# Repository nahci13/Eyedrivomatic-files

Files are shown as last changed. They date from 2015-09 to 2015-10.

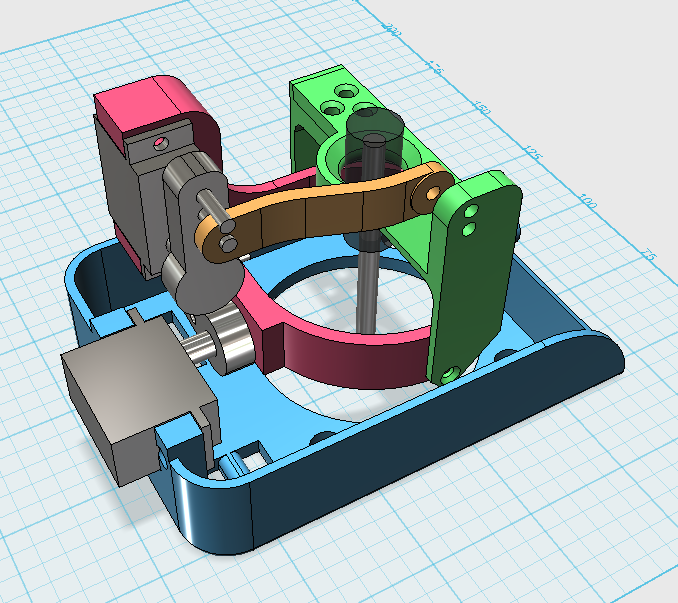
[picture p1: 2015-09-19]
Eyedrivomatic Photos/mk5 electronic hand design.png

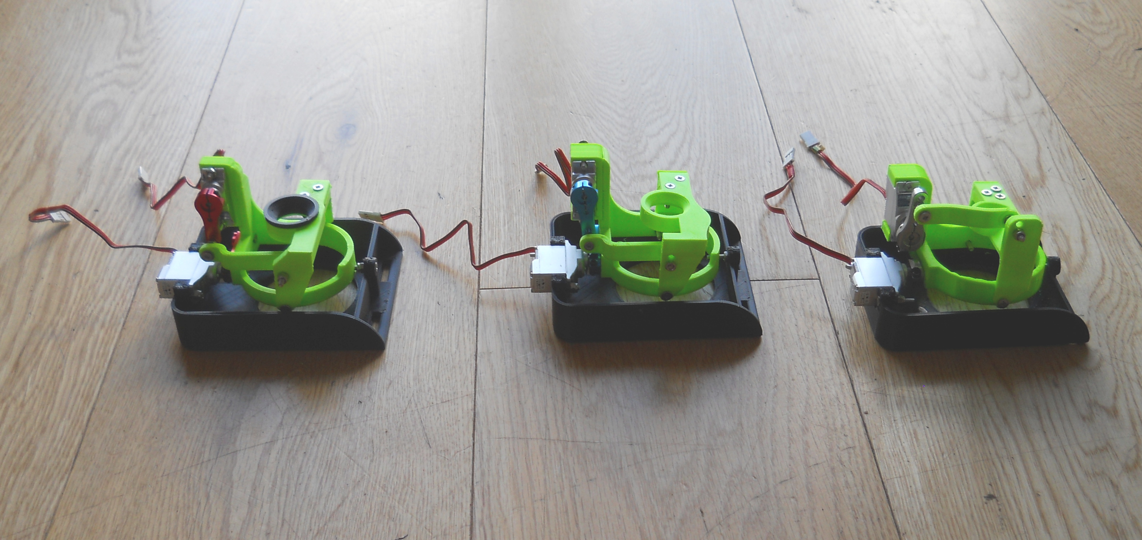
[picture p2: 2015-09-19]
Eyedrivomatic Photos/electronic hand sub prototypes.JPG

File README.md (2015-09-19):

# Eyedrivomatic-Pure
All the files needed to build an Eyedrivomatic system 

Eyedrivomatic is a low cost system to enable quadraplegics to drive an electric wheelchair using only their eyes. In this repository are all the files needed to build an eyedrivomatic system yourself. An eyedrivomatic system is made up of two parts; a 'brain box', and an 'electronic hand'. The electronic hand physicaly pushes the wheelchair's joystick, and the brain box controls it. Software on the users computer, controlled by eyegaze equipment, sends commands to the brain box. 

All the software for the eyedrivomatic project is free software: you can redistribute it and/or modify it under the terms of the GNU General Public License version 3.For more info see http://www.gnu.org/licenses/

all the hardware for the eyedrivomatic project, and the 3d design files and stl files necessary to produce the hardware are licensed under a Creative Commons Attribution-ShareAlike 4.0 International License. For more info see   http://creativecommons.org/licenses/by-sa/4.0/

This repository has all the necessary files, however at present there are no build instructions. I will produce build instructions over the next few weeks and upload them here. 

Patrick Joyce 1/August/2015

DISCLAIMER

The Eyedrivomatic System is potentially dangerous if used without proper caution. Neither myself, nor any member of the Eyedrivomatic team accept any responsibility whatsoever for any injuries to persons, or damage to property sustained during the use, or misuse of Eyedrivomatic. Use of The Eyedrivomatic System is entirely at the users own risk. 

To ensure safe operation, the following guidelines MUST be adhered to at all times; 

Users MUST be supervised at all times. 
The area of use MUST be entirely flat 
The area of use MUST be devoid of people, animals or any other potential hazards. 
The area of use MUST NOT have any hazards at it's boundaries - i.e. slopes of any kind, water, steps leading down, roads, people, anything that could be damaged by an out of control wheelchair, anything that could damage the occupant of an out of control wheelchair, etc.

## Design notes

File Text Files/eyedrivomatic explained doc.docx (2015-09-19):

I can’t talk any more. I can make individual words understood, but it’s not what you would call talking. The only method I have left for controlling the computer, and what I now use for communicating, is a bluetooth wheelchair joystick, which works wirelessly as a mouse. This method soon will no longer work as MND/ALS is weakening my hand relentlessly to the point of uselessness.

I live in the UK, and our wonderful NHS has provided me with an electric wheelchair and, for when my hand does become useless, a wheelchair mounted minicomputer with an eyegaze camera. But the NHS does not allow you to control the one with the other. Control a wheelchair with your eyes - far too dangerous! Much better that you just sit where you are sir, much safer. Once you have only your eyes left they expect you to rely on your carer to move your wheelchair. If your carer is not available you stay where you are left. My MND/ALS has a slow progression rate, so when I reach that point I will remain like it for two or three years. Two or three years without being able to move, it makes me shiver with horror just to think about it.
I want to be in charge of my own life and remain as independent as possible for as long as possible, right until the end. And I am not alone. There are a multitude in my position and many more in a worse one.
It would be possible to control the wheelchair straight from the computer, to interface them directly. But I don't own either unit, and they won’t be pleased if I cut them up. Also, a solution like that would work for me but wouldn't work for anyone else. So I have designed a bolt on, one size fits all system that the mini computer can talk to via infrared, and which would then physically move the joystick on the wheelchair.
I have a piece of software on my minicomputer called grid 2. It is primarily communication software but it also does infra red environmental control. This is intended for controlling your telly and things like that by emulating a remote control. Grid2 is s a really good package because it allows the user to easily configure new pages for doing different jobs. Like, in this case driving my wheelchair with my eyes.

I built a prototype with a cardboard case and some parts kindly 3d printed by a follower from my facebook page. This allowed me to test it and prove the concept. I printed a prototype case for brains of the thing and one for the IR unit. The system is complete and works, it can easily be put together without soldering by anyone, even an idiot, for less than £70, which is about one hundred of your American dollars. My idea is to make it open source, put the plans, software and instructions on the internet for anybody to use. There are thousands of people who would benefit from this, thousands of people who are stuck in the same place, immobile unless their carers move them.
The prototype works but it’s not ready to distribute. The working parts need to be redone as does the case. The firmware needs rewriting and when that’s done I need to build two or three units for real world testing.

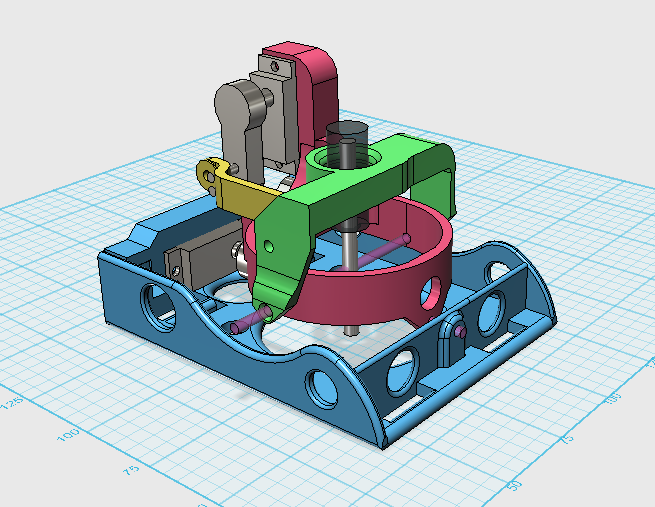
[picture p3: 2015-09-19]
Eyedrivomatic Photos/Mk5b-Electronic_hand_design.png

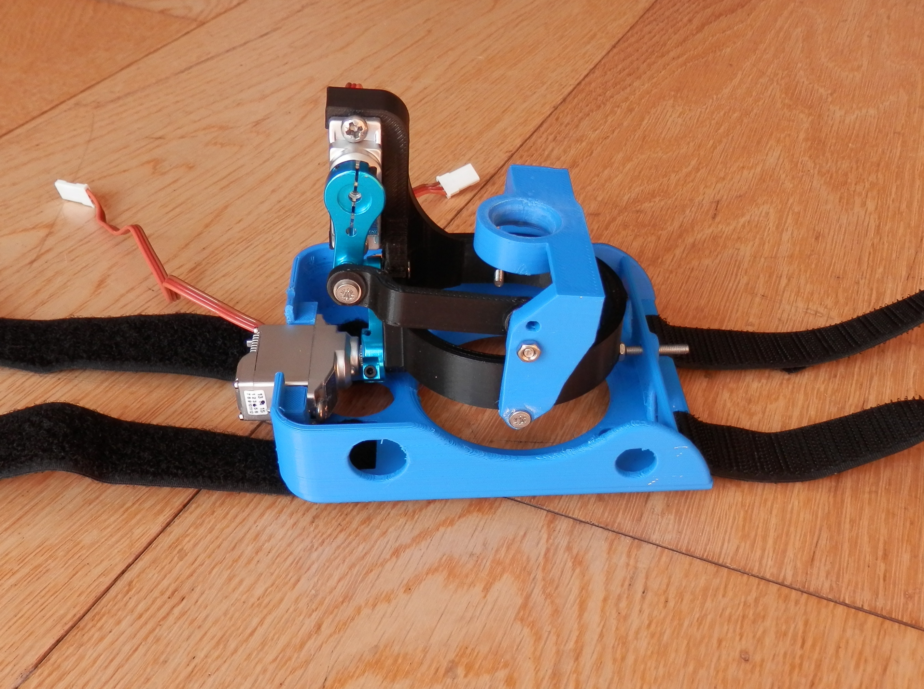
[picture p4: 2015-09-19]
Eyedrivomatic Photos/mk5b electronic hand2.JPG

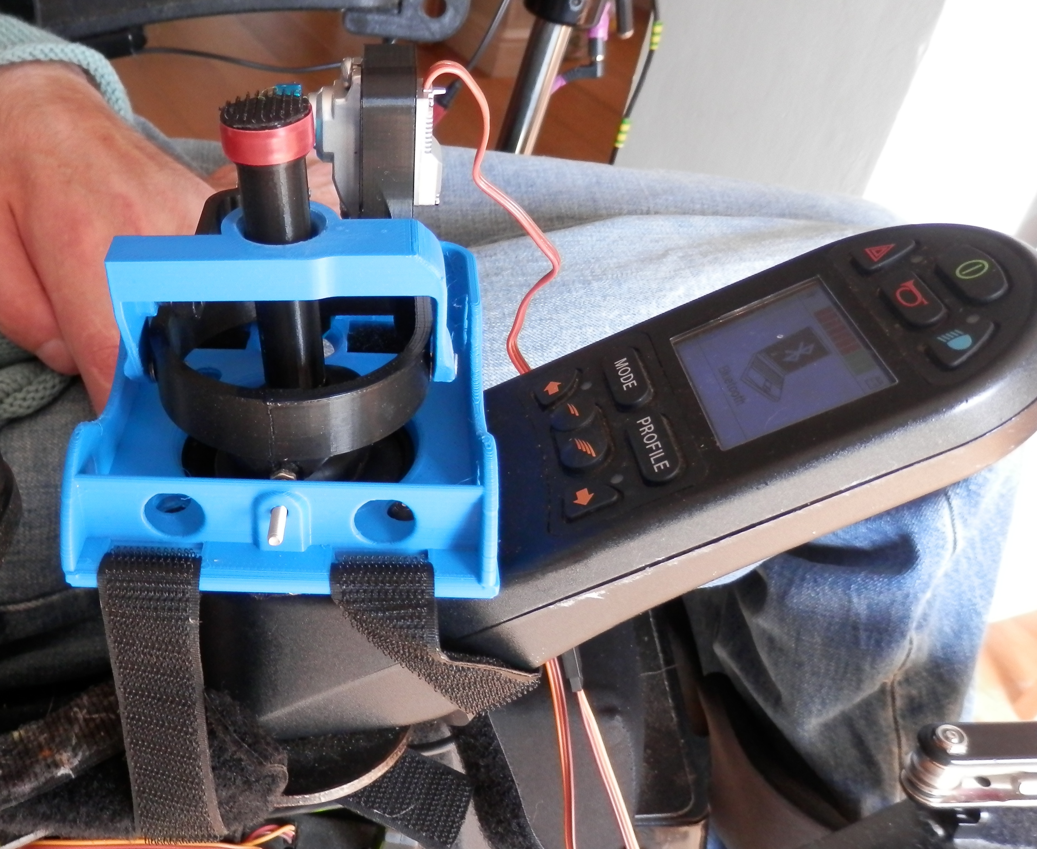
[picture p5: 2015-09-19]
Eyedrivomatic Photos/mk5b electronic hand1.JPG

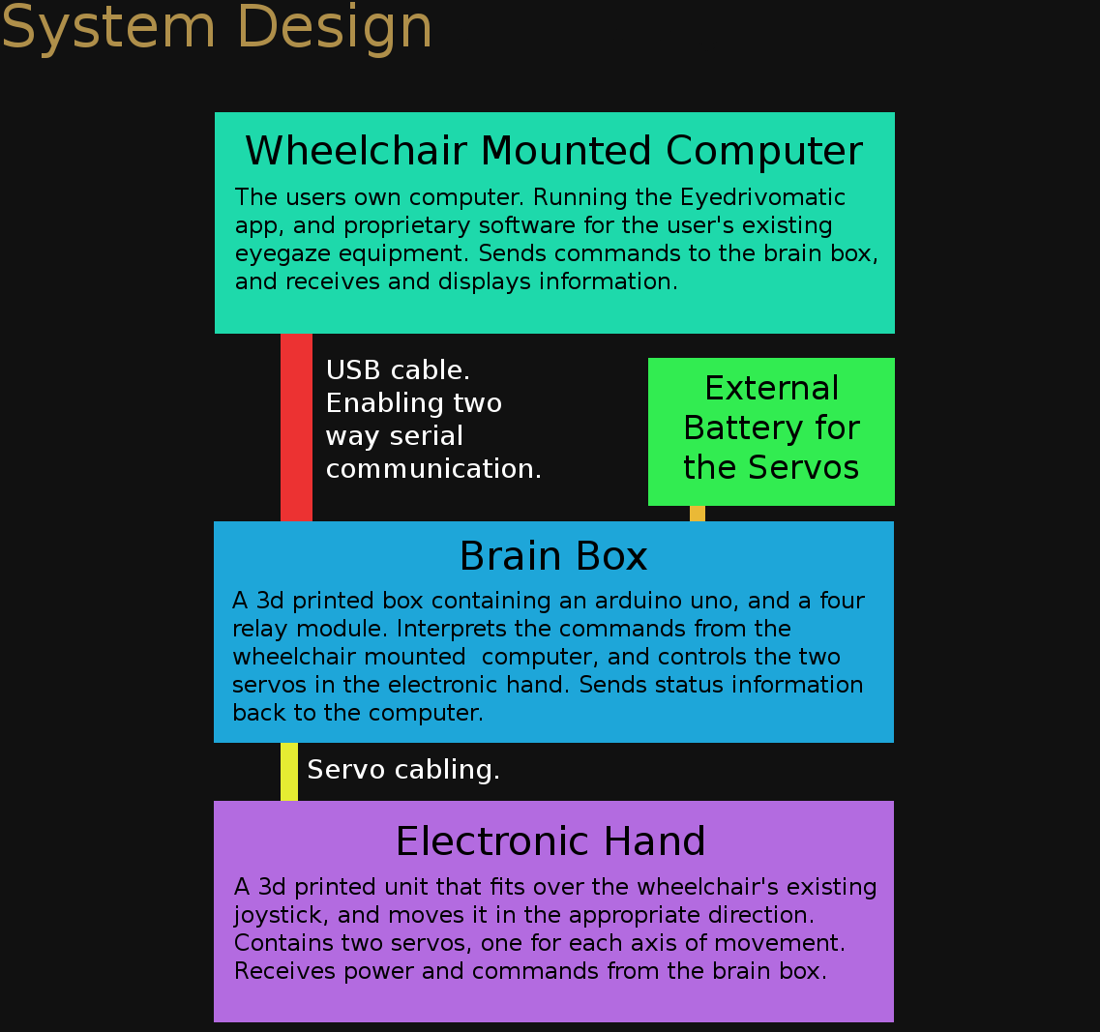
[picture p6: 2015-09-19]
Eyedrivomatic Photos/eyedrivomatic system design document.png

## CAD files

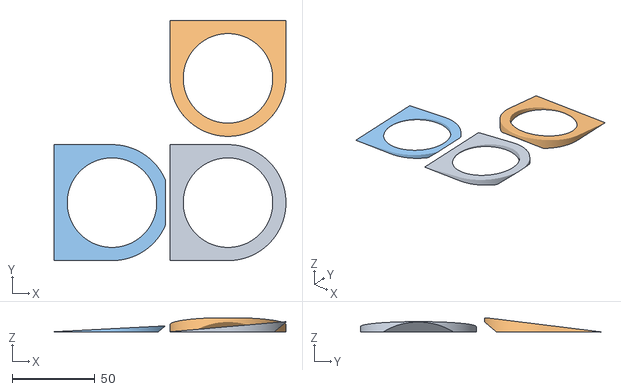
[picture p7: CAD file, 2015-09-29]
stl files/LocatorWedges.stl
140.0 x 145.0 x 8.50

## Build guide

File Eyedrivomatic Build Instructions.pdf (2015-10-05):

# Eyedrivomatic Build Instructions

## Copyright Patrick Joyce 2015

These instructions are licenced under creative commons

Attribution-ShareAlike 4.0 International (CC BY-SA 4.0)

What you will need.

For one complete Eyedrivomatic System (one brain box, electronic hand, and adjustable locator)

1 x Arduino Uno R3
1 x 3d printed parts for brain box (base plate, lid, and two cable retaining pieces)
1 x 3d printed parts for Electronic hand (base piece, X servo carrier, lower ring, Y servo carrier, upper ring, transmission arm)
1 x 3d printed joystick sleeve (the correct internal diameter to snugly fit your joystick shaft)
1 x 3d printed parts for adjustable locator plate (lower ring, upper ring, retaining ring)
2 x Turnigy 380Max Micro servo (or similar high torque micro servo)
2 x metal 25t servo arms (the design calls for a specific model, see illustration)
1 x relay shield (the design calls for a specific model. Please see illustration below)
1 x servo/sensor shield (the design calls for a specific model. Please see illustration below)
1 x USB A to USB B cable (length required depends on where your brain box will be located) 1 x USB A to DC plug (the particular type of DC plug isn't important, as it will be removed) 2 x servo extension cables, male to female (again length required depends on location)
20 x No6 Pan head, Pozi self tapping screws 13mm
10 x No6 Pan head, Pozi self tapping screws 16mm
10 x M3 bolt, countersunk, pozi
10 x M3 nyloc nut
10 x M3 flat washers
1 x self adhesive hook and loop tape. 20mm wide. 60cm of hook and the same of loop 1 x Super Glue
1 x double sided foam tape (5 or 10mm wide, or cut down from a wider roll)

Build Instructions

1) Adjustable locator

The adjustable locator is permanently fixed to the wheelchair's joystick unit with double sided foam tape. It provides a reliable and accurate mounting point for the electronic hand. Should it no longer be required, it can be easily removed without damaging the chair.

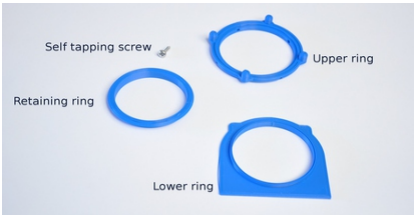
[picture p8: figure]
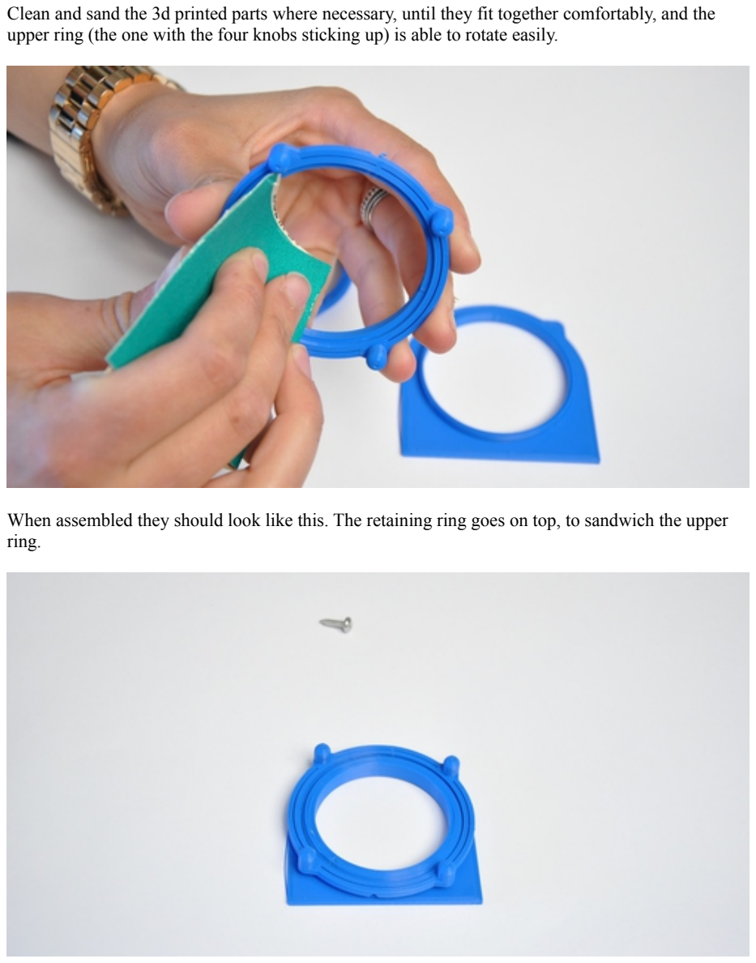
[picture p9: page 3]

Clean and sand the 3d printed parts where necessary, until they fit together comfortably, and the upper ring (the one with the four knobs sticking up) is able to rotate easily.

When assembled they should look like this. The retaining ring goes on top, to sandwich the upper ring.

Then remove the retaining ring, and put some glue around the inner face of the bottom ring. Then replace the retaining ring. This will glue the retaining ring to the bottom ring, while still allowing the upper ring to rotate freely.

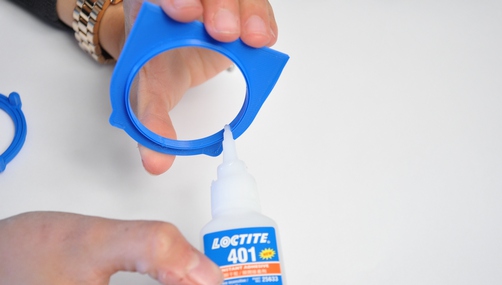
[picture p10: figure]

When the glue has set, insert a self tapping screw into one of the locking screw holes (where it will be accessible when on the chair) and tighten it up until the upper ring will no longer move.

Locator wedges (optional)
The locator needs to be installed on the joystick unit, perpendicular to the joystick shaft. Many joystick units have the joystick shaft perpendicular to the unit's upper surface. If you have one such unit, then you will not require a wedge. If however your joystick leans forward relative to the joystick unit, then you will need a wedge to level the locator relative to the shaft.

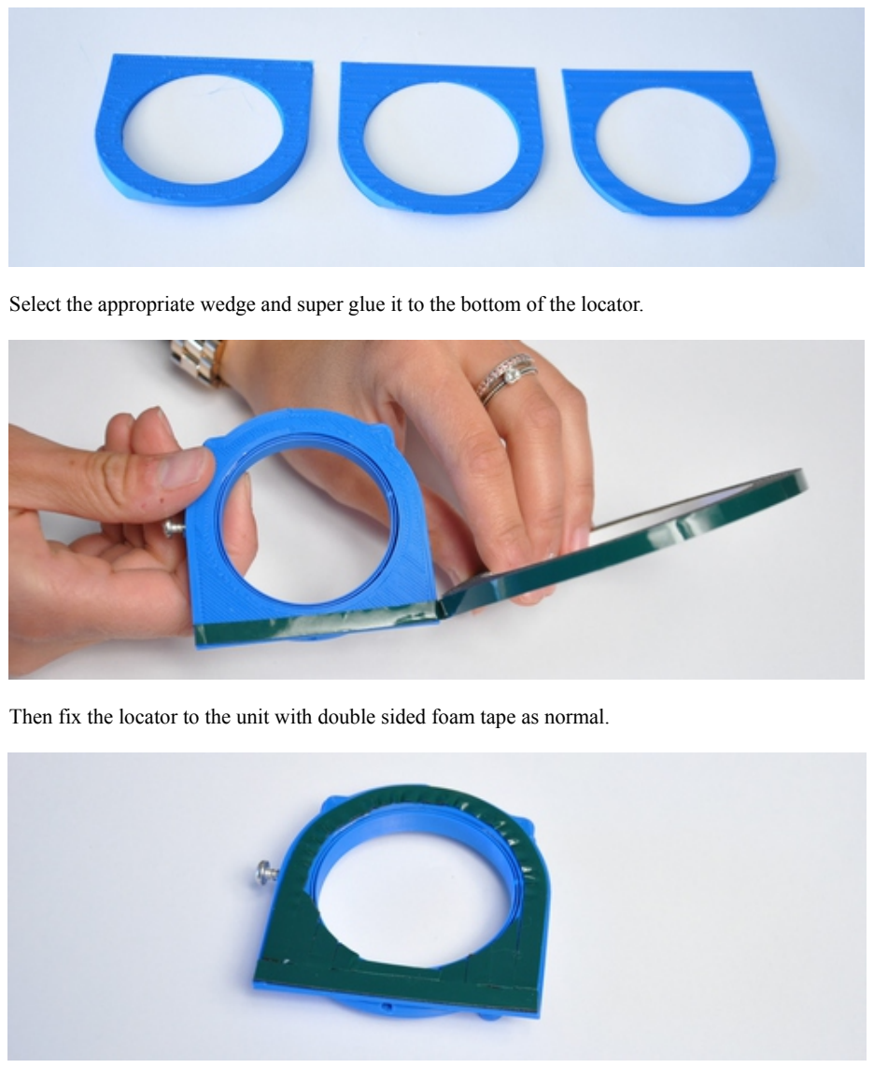
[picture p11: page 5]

Select the appropriate wedge and super glue it to the bottom of the locator.

Then fix the locator to the unit with double sided foam tape as normal.

2) Brain Box

first, assemble the four 3d printed parts needed and sand and clean up where necessary.

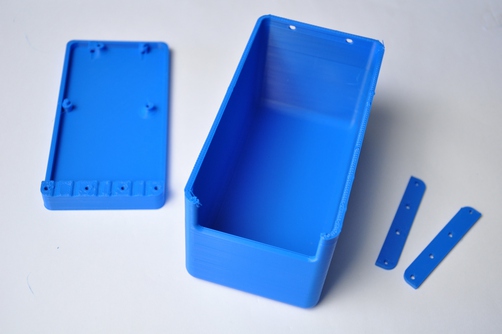
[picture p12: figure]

Set the lid and the two cable retaining plates aside.
There are three printed circuit boards needed for the brain box, which should look like this;

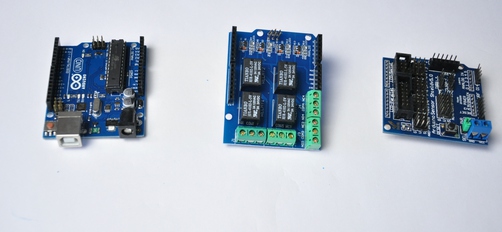
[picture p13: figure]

From left to right they are; Arduino uno, relay shield, and servo/sensor shield.
Fit the arduino on to the base plate. There are four holes in the arduino, which correspond to two pegs, and two holes in the base plate. Locate the arduino on the pegs and secure it with two self tapping screws.

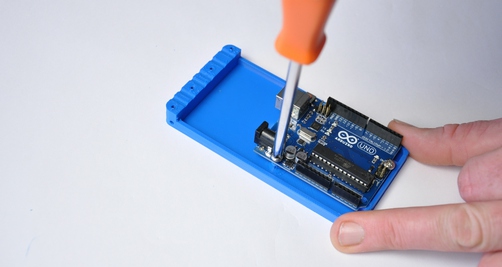
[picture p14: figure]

Then insert the usb cable into the arduino. Next we have to fit the relay shield. It has rows of pins underneath it which fit into the rows of sockets on the arduino.

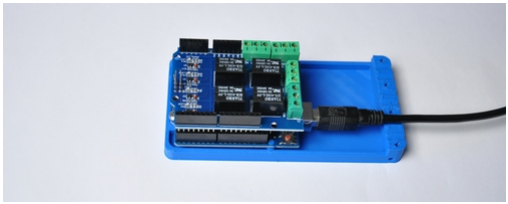
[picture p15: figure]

The pins don't go all the way in, but they go in pretty far – see illustration. Careful not to bend them.
Next is fitting the output sockets. The output sockets are 3.5mm mono headphone sockets, with 17cm of cable attached. Cut them down from mono extension cables, or headphone splitter cables. Just make sure they're mono, not stereo. You will need three. Now, prepare the ends of the cables. Strip them, and twist the ends. Most cables like this will be coaxial, meaning that there will be an inner core which has its own insulation. Around that is a multi strand conductor. Twist that together and that is your second core. Each core needs to be about 8mm long before it disappears into the insulation. And the inner core insulation needs to stick out beyond the outer sheath by about 8mm as well. Bend your 8mm twisted ends in half, so you now have 4mm ends.
Now fit the three output sockets to the green terminal blocks on the relay shield.

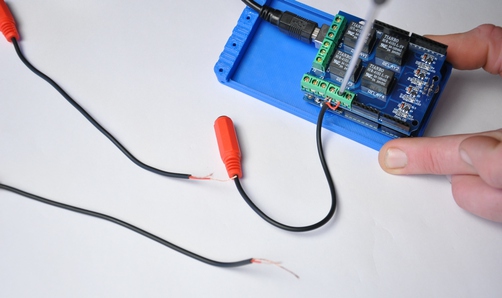
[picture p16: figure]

The terminal blocks are numbered on the relay shield, one to four. Connect the three output sockets to number one, three and four. Each block has three connection holes, marked NO, COM, and NC. Connect each socket into NO and COM. It doesn't matter which wire goes in COM, and which goes in NO. In the above photo Ben is fitting an output socket to terminal block number four. It is important that there is very little bare wire outside the terminal block, and no insulation inside the terminal block.

In the above photo, the socket attached to terminal block number four is attached correctly. The ones attached to blocks one (at the top of the photo) and three are not. There is excessive bare wire outside the terminal block, which could lead to a unintentional short circuit. Which would be bad. Next we need to prepare the usb power cable. This looks like this;

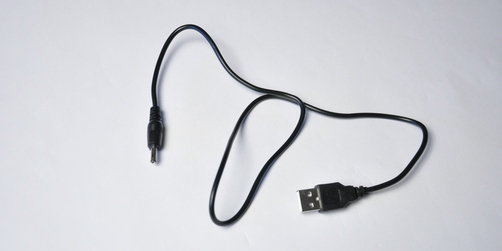
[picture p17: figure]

or similar. We have to cut off the DC plug, and depending on where you want to site your power source, maybe some of the cable as well. Then strip and twist the end.

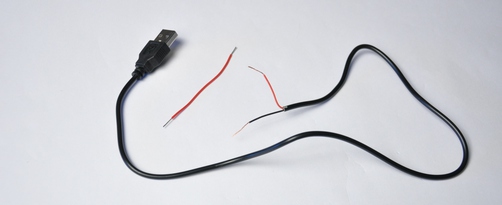
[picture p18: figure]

If you're lucky, as I was, you will have one core with red insulation, and one with black. Red is positive, and black is ground. If you're not lucky, you'll have to find out the cable polarity with a multimeter. You will also need a short piece of of cable with stripped ends, as in the photo – say 6cm long.
Now connect the red (positive) wire from the usb power cable to NO on terminal block number two. Then attach the short piece of wire to COM. As in the photo below.

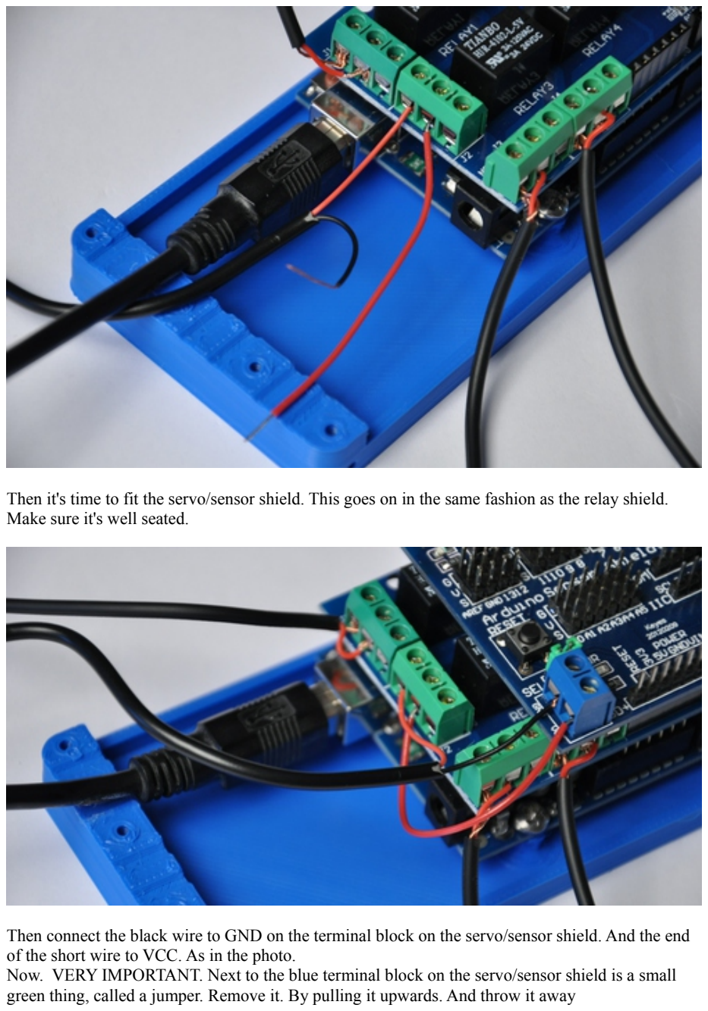
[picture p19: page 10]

Then it's time to fit the servo/sensor shield. This goes on in the same fashion as the relay shield. Make sure it's well seated.

Then connect the black wire to GND on the terminal block on the servo/sensor shield. And the end of the short wire to VCC. As in the photo.
Now. VERY IMPORTANT. Next to the blue terminal block on the servo/sensor shield is a small green thing, called a jumper. Remove it. By pulling it upwards. And throw it away

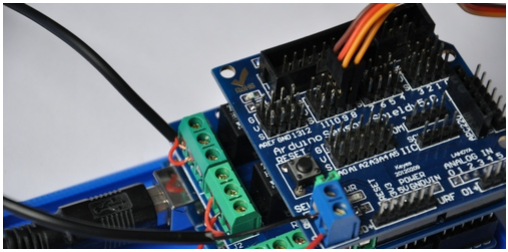
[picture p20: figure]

Next we will attach the two servo extension cables. On the servo/sensor shield is three rows of pins. The three rows are labelled G, V, and S. In the other direction they are labelled 0 – 13. The two plugs need to go into rows eight and nine. It is essential that the yellow or white wire is in the row marked S. The black or brown wire must be in the G row.
The next stage is securing the cables in the two storey cable retainer.

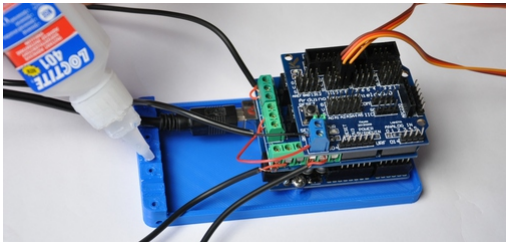
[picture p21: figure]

The lower storey is for all the wires except the servo cables. First put a little super glue in each of the little cable channels printed in the base plate. Then lay one cable in each channel. There is one spare channel. Ignore it. Then sit the lower retaining plate on top. The lower plate has channels printed in it too. Place it flat side up. Then screw it in place with self tapping screws. It should look like the photo below.

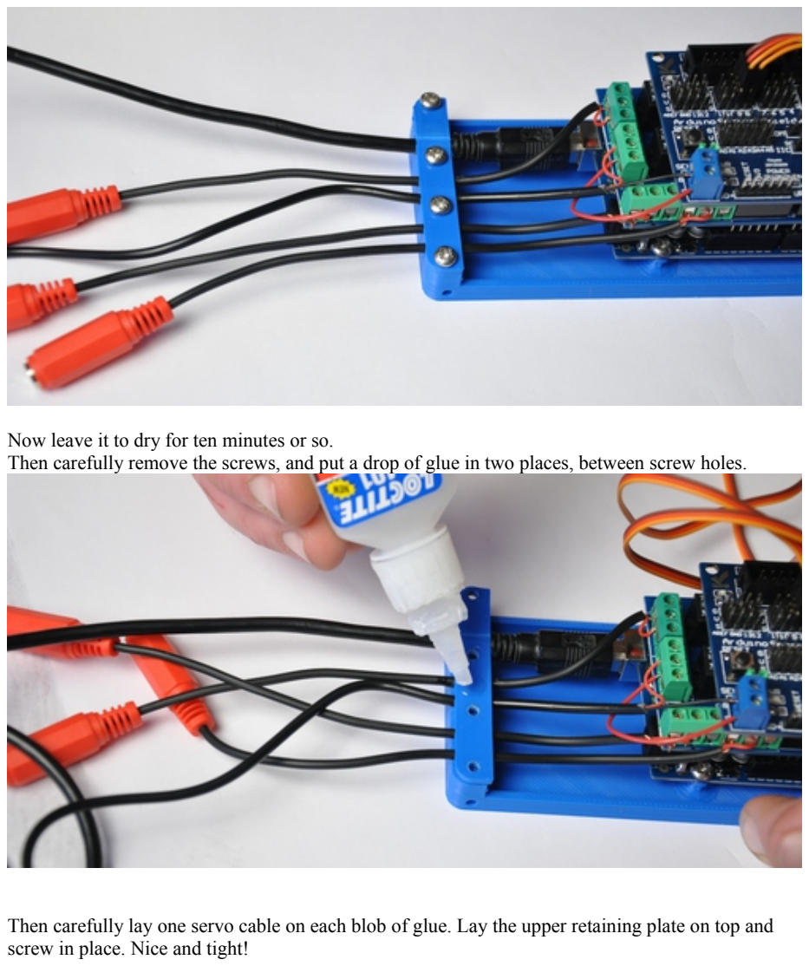
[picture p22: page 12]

Now leave it to dry for ten minutes or so.
Then carefully remove the screws, and put a drop of glue in two places, between screw holes.

Then carefully lay one servo cable on each blob of glue. Lay the upper retaining plate on top and screw in place. Nice and tight!

At this point it's well worth labelling your output cables. The servo cable in number eight is called X, and the other Y. The three output sockets are labelled 1, 2, and 3. N'umber one is in terminal block number one, number two is in terminal block number three, and number three is in terminal block number four. The usb cable going in to the arduino should be labelled 'To PC'. The other, thinner usb cable, label 'servo power only'.

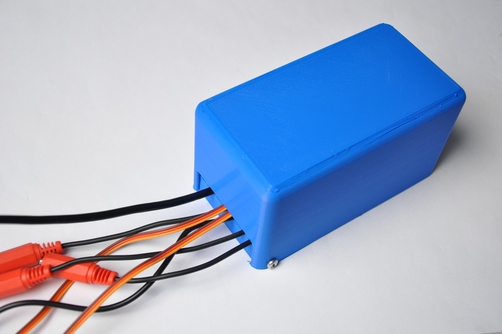
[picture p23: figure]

Then whack the lid on, secure it with four screws, and have a cup of tea. The brain box is finished, and ready for firmware.

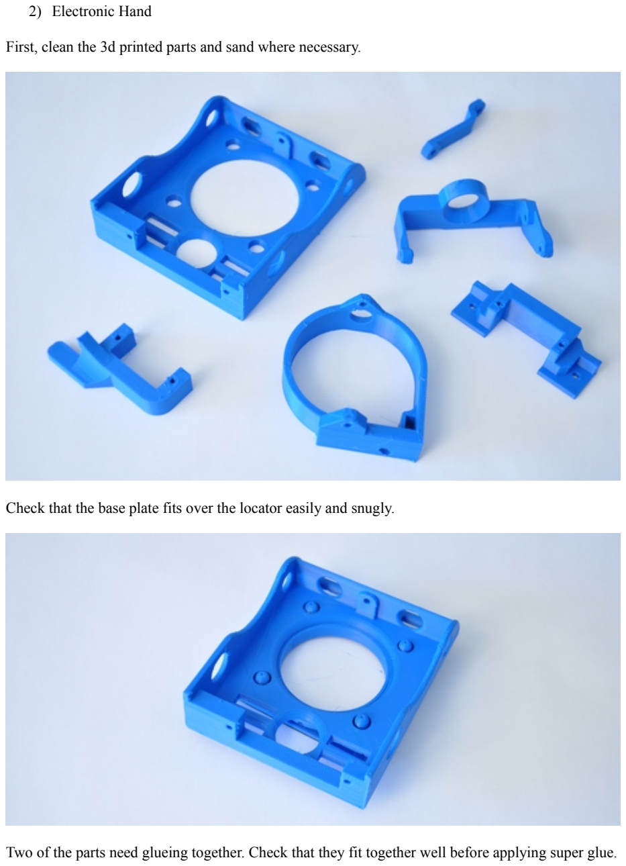
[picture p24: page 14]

2) Electronic Hand

First, clean the 3d printed parts and sand where necessary.

Check that the base plate fits over the locator easily and snugly.

Two of the parts need glueing together. Check that they fit together well before applying super glue.

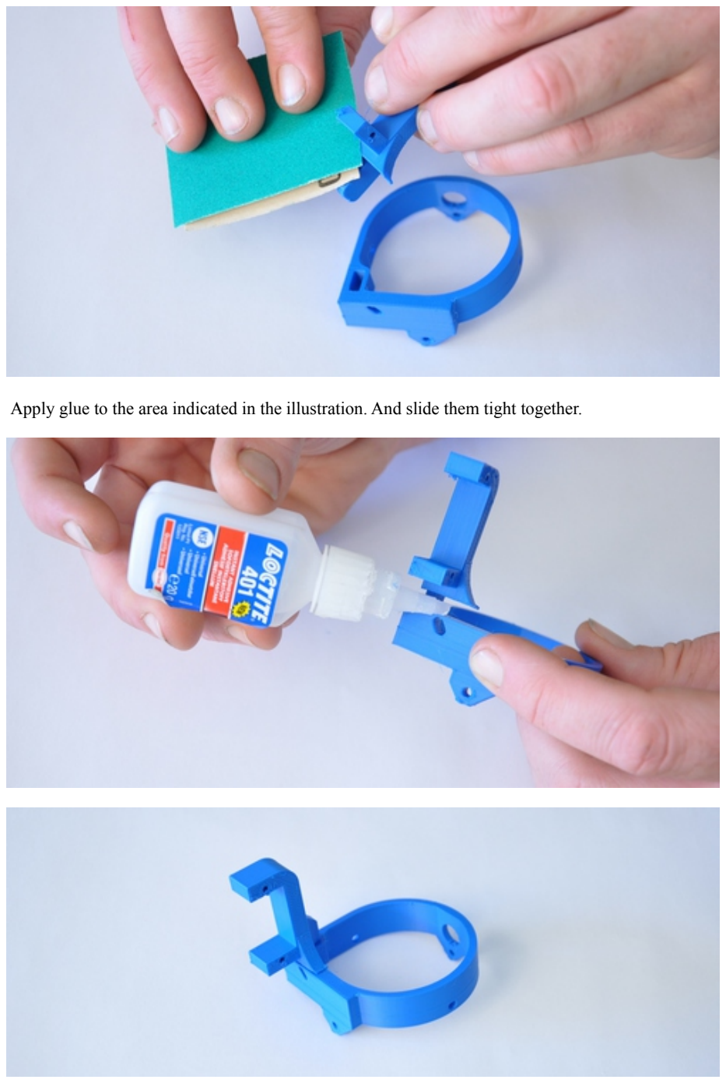
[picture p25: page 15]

Apply glue to the area indicated in the illustration. And slide them tight together.

While those parts are drying, insert an m3 bolt into one side of the upper ring cradle. When it's nearly all the way in, add a drop of glue to the thread, then screw it all the way in. Then set aside.

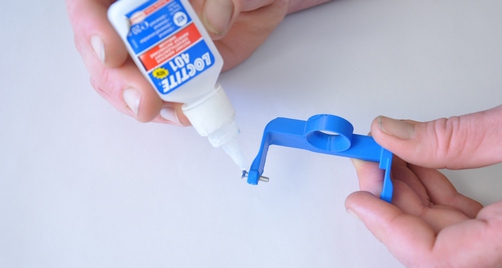
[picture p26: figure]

Then put a bolt in the side hole of the lower ring, facing outwards. Glue it in, in the same fashion.

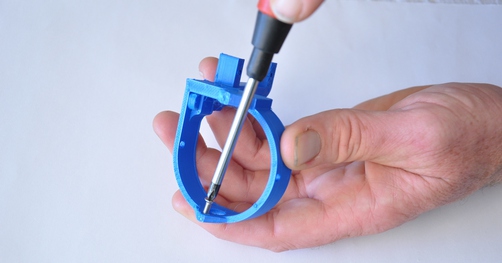
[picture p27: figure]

When everything is dry, fit the side of the upper ring cradle to the lower ring. Make sure the cradle is the right way round. Then glue another bolt into the other side of the cradle, securing it in place.

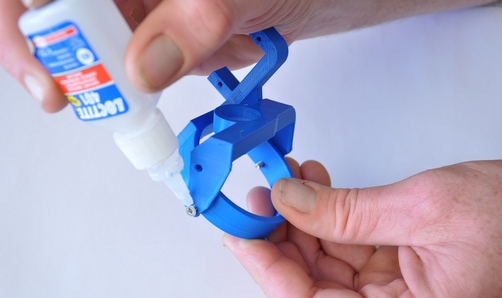
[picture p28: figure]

It should move freely from side to side, but not forwards and backwards. Allow everything to dry. Now screw one servo to the servo carrier, and one to the lower ring assembly. Make sure both servos are the right way round.

Now we have to centre the servos. This requires you to upload the firmware to the Brain Box, and the software to your PC. This process is covered in a separate instructable. Then you run the software, with the servo cables and a servo power source attached. Navigate to 'trim' and both servos to ninety degrees. Then go to the driving controls and check both servos are moving when you play with the direction buttons.

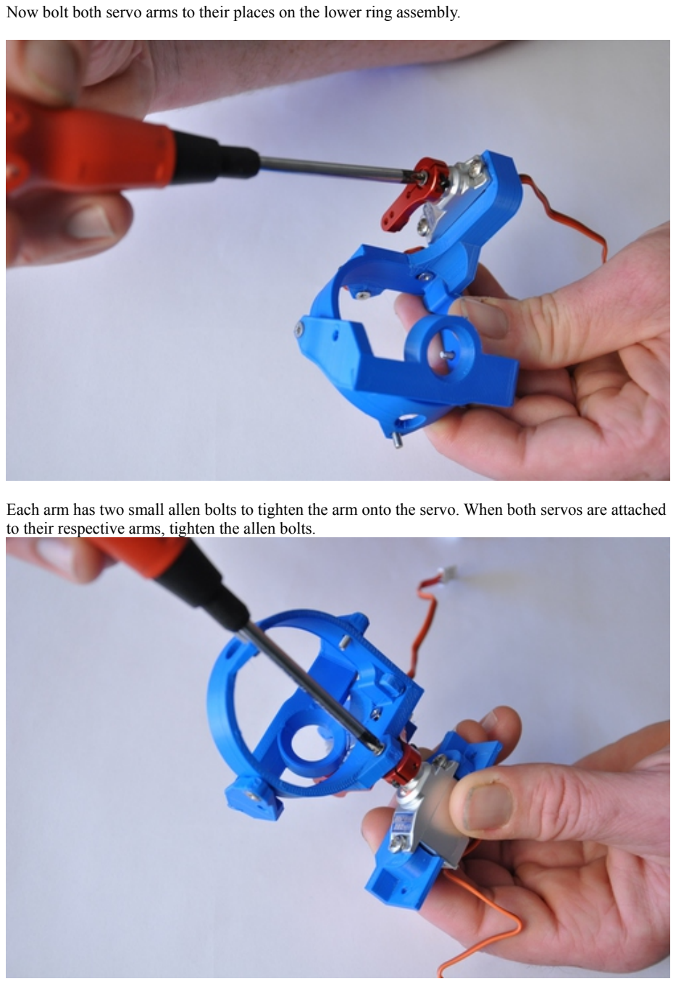
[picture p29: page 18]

Now bolt both servo arms to their places on the lower ring assembly.

Each arm has two small allen bolts to tighten the arm onto the servo. When both servos are attached to their respective arms, tighten the allen bolts.

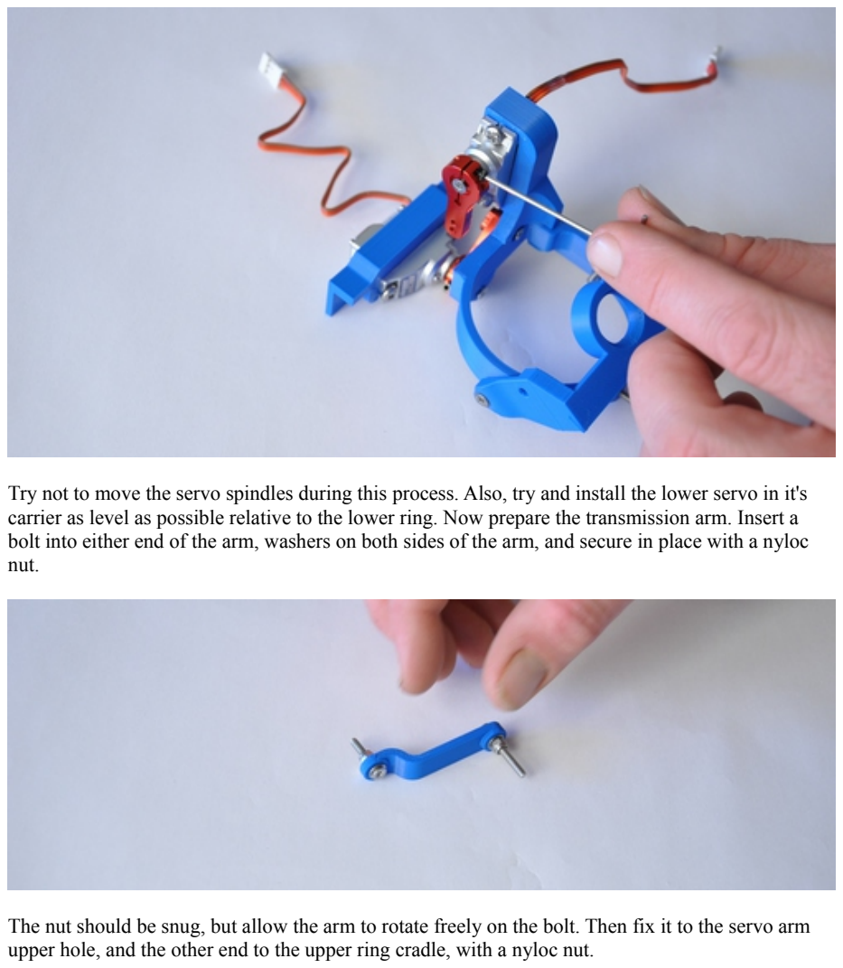
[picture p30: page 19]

Try not to move the servo spindles during this process. Also, try and install the lower servo in it's carrier as level as possible relative to the lower ring. Now prepare the transmission arm. Insert a bolt into either end of the arm, washers on both sides of the arm, and secure in place with a nyloc nut.

The nut should be snug, but allow the arm to rotate freely on the bolt. Then fix it to the servo arm upper hole, and the other end to the upper ring cradle, with a nyloc nut.

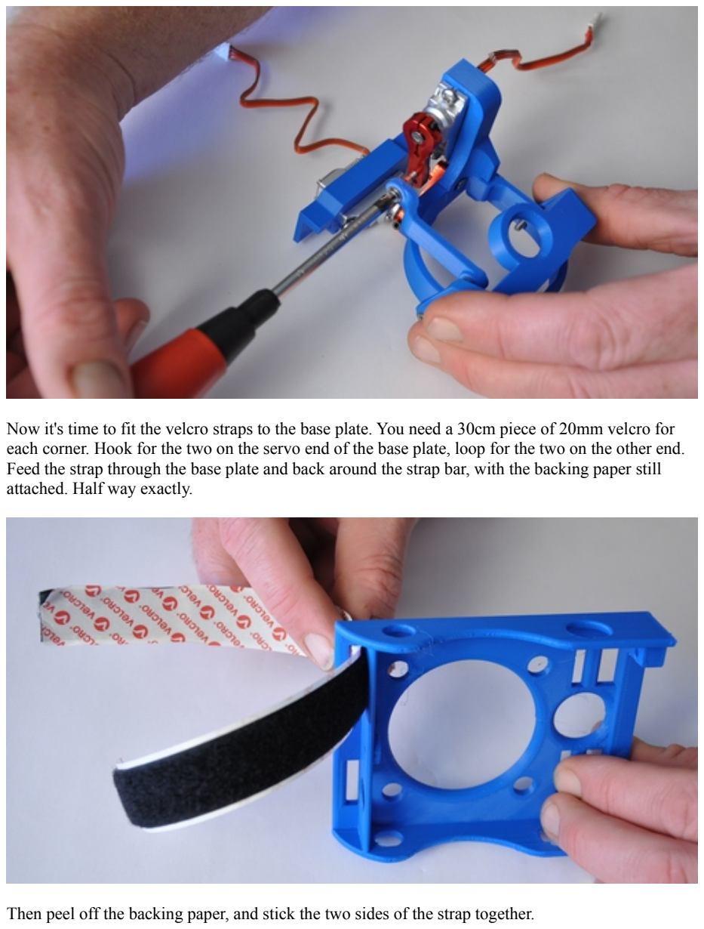
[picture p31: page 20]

Now it's time to fit the velcro straps to the base plate. You need a 30cm piece of 20mm velcro for each corner. Hook for the two on the servo end of the base plate, loop for the two on the other end. Feed the strap through the base plate and back around the strap bar, with the backing paper still attached. Half way exactly.

Then peel off the backing paper, and stick the two sides of the strap together.

Then repeat the process till you've done all four.
Finally, insert the protruding bolt on the lower ring into the corresponding hole on the base plate. Slot the servo carrier into place on the base plate, and screw in with two self tapping screws.

And you're done!

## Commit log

2015-09-19 semi finals update
    [eyedrivomatic_brain_box_lid.stl, mk1_evans_locator.stl]
2015-09-29 minor update
    [LocatorWedges.stl]
2015-10-04 build instructions pdf
    [mk1_evans_locator.stl]
